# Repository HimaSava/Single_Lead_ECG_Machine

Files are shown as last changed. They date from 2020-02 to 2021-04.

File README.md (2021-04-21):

# Single_Lead_ECG_Machine

This project started as the project component for my subject analog electronic communcation that I took in my Winter Sem 2019.

The project uses 3 wires to be connected to the paitent as to aquire the ECG waveform from 2 of them and the third used as ground. The Circuit uses basic filteration techniques to get rid of the surrounding noise and amplify the signal to be effectively seen on a osciloscope.

## Components of the Circuit and thier purpose:
#### 1. Instrumentational Amplifier:
The ECG signal received from the body is in milivolts and thus needs to be amplified in order to be captured by any instrument. An instrumentational amplifier is used rather than an normal amplifier as it helps limit the noise entering the system due to its differential amplification functionality.

#### 2. High Pass Filter:
A high pass filter is used to get rid of the lower frequencies caught up in the system. This filter also takes care of the dc voltage in the system, avoiding saturation of the furthur amplification stages. An second order filter is used for better results.

#### 3. Low Pass Filter:
A low pass filter as expected is again used to remove the unnecessary frequencies. A second order filter is used for optimised results.

#### 4. Notch Filter:
A notch filter is a filter that helps remove a very narrow band of frequencies. In our case it is tuned for 50Hz. This is the standard AC freq. in the Indian power supply and thus is present in the surrounding in great quantities. This is caught in the system and can lead to distorting the final waveform significantly.

## Components used:
#### 1. OpAmps TL074CN (Highly advised for this experiment)
#### 2. Registers 
#### 3. Bi-Directional Capacitors(Ensure the cap are not uni-directional as the ECG signal is bi-directional)

## Tools used:
1. Multisim - To design and test the basic circuit.
2. Eagle AutoCAD - To design the custom PCB and help design the soldering breadboard circuit layout.

## Scope for improvement:
#### Currently the waveform is only viewed using an osciloscope, but in future I want to connect the system to my laptop and record data using it. For this a few more components need to be added to the ciruit as listed below:

1. Level Shifter:
An Analog to digital converter can only deal with positive voltages thus the waveform needs to be shifted upwards to convert the negative part of the ECG signal to positive.

2. A2D converter:
An analog to digital converter is needed as our output is analog but the inut by the microcontroller can only be digital.

3. Microcontroller:
An microcontroller will be able to accept the input from the A2D converter and using Communcation protocols as Serial(RS232), ICP, etc transfer the data to the PC.

4. PC end program:
Once we start recieving the data from the circuit it is important to store the same and show the output in the most familier fashion of an graph. This will be handled by an PC end program.

#### A custom designed PCB will also help in reducing the noise in the system.

### Pls find the attached in the folders above:
1. Individual Circuits of the filters
2. The complete Circuit for the ECG.
3. Eagle files for the PCB (Gerber files will be added shortly)
4. Output waveforms captured by the circuit and the final pictures of the circuit.

Manufactured Layout V1.0

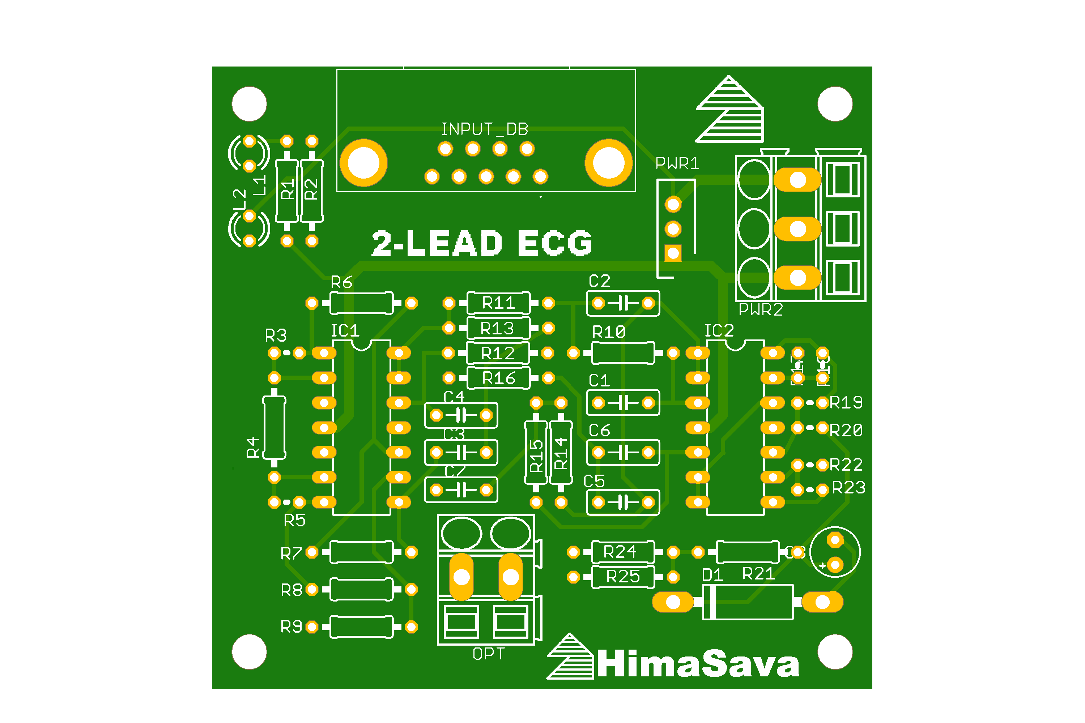
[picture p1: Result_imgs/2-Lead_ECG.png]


Output!!

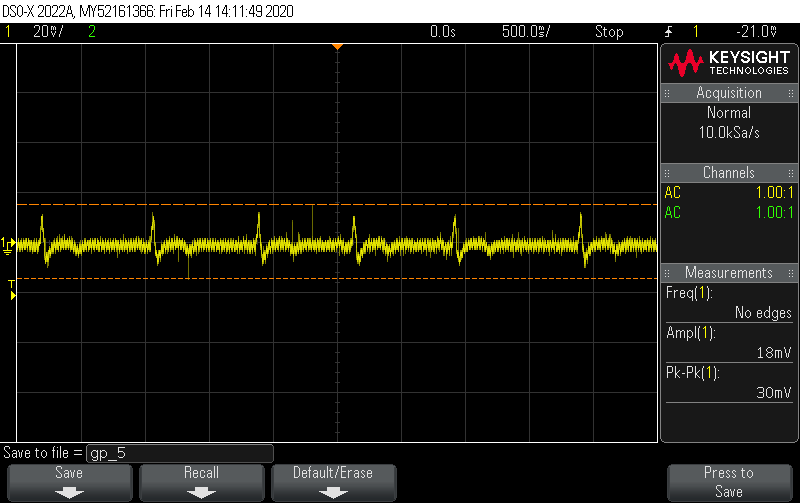
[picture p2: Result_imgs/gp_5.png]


#### -Himanshu Savargaonkar
##### P.S. Shoutout to Praneeth G (gp201) for being the test subject for all the live tests conducted in the debugging phase :)

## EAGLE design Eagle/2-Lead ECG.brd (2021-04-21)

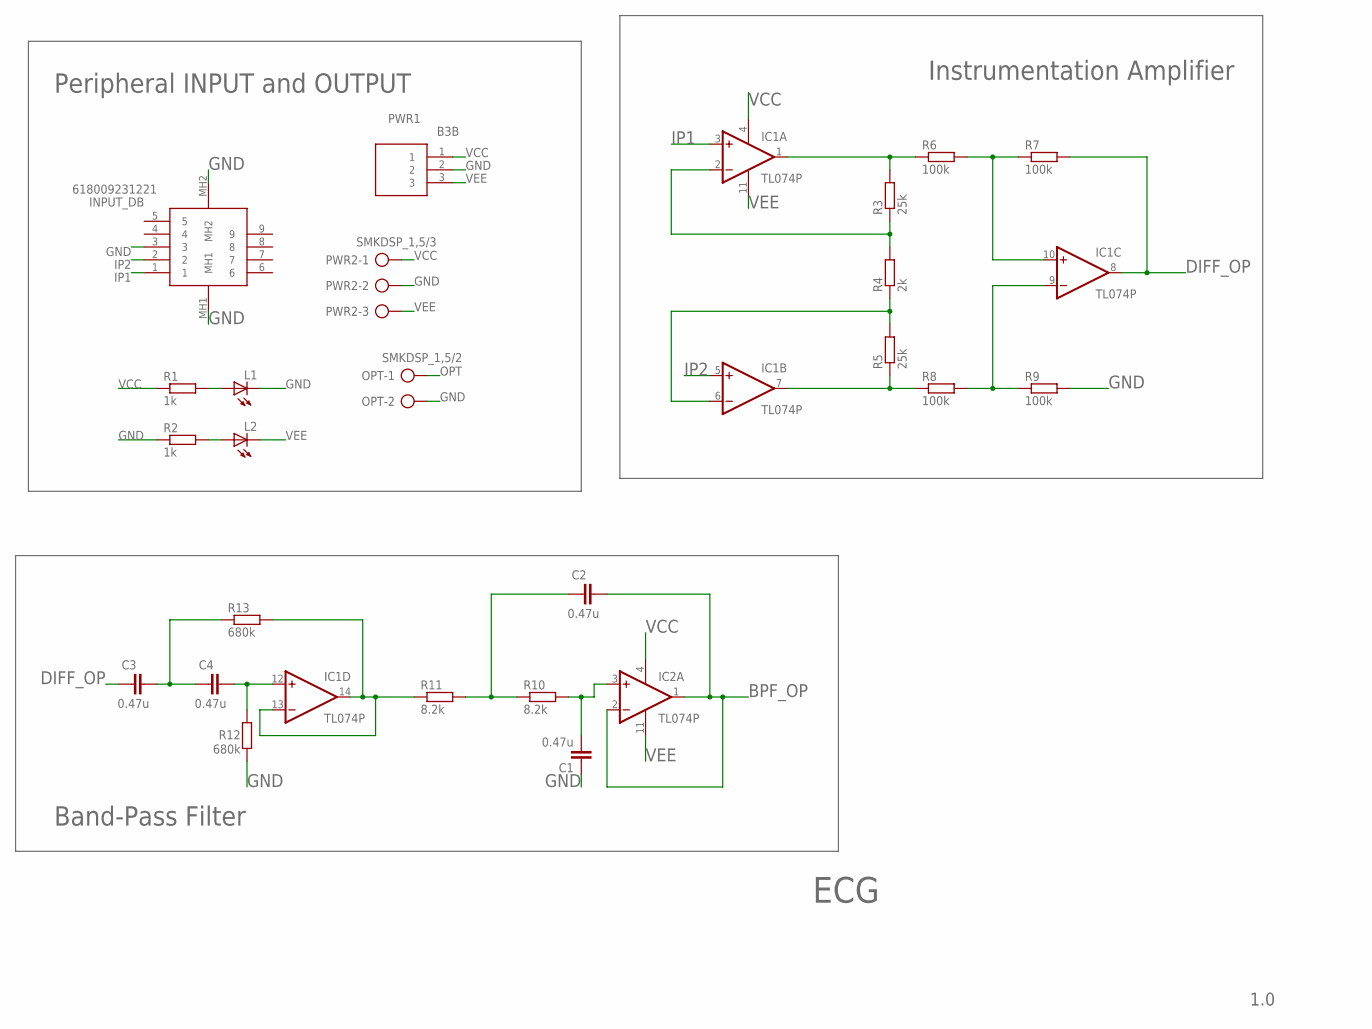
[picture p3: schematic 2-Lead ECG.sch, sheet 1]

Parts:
C1, C2, C3, C4: 0.47u; C050-025X075
IC1, IC2: TL074P; DIL14
INPUT_DB: 618009231221
L1, L2: LED3MM
OPT: SMKDSP_1,5/2
PWR1: B3B; SHDR3W64P0X250_1X3_1000X380X60
PWR2: SMKDSP_1,5/3
R1, R2: 1k; 0207/10
R3, R5: 25k; 0204V
R4: 2k; 0207/10
R6, R7, R8, R9: 100k; 0207/10
R10, R11: 8.2k; 0207/10
R12, R13: 680k; 0207/10

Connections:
BPF_OP: C2.2, IC2.1 (OUT), IC2.2 (-IN); also elsewhere on the board
DIFF_OP: C3.1, IC1.8 (OUT), R7.2
GND: C1.1, INPUT_DB.3, INPUT_DB.MH1, INPUT_DB.MH2, L1.K (C), OPT.2, PWR1.2, PWR2.2, R2.1, R9.2, R12.1; also elsewhere on the board
IP1: IC1.3 (+IN), INPUT_DB.1
IP2: IC1.5 (+IN), INPUT_DB.2
unnamed: L1.A, R1.2
unnamed: L2.A, R2.2
unnamed: IC1.1 (OUT), R3.2, R6.1
unnamed: IC1.2 (-IN), R3.1, R4.2
unnamed: IC1.6 (-IN), R4.1, R5.2
unnamed: IC1.7 (OUT), R5.1, R8.1
unnamed: IC1.10 (+IN), R6.2, R7.1
unnamed: IC1.9 (-IN), R8.2, R9.1
unnamed: C3.2, C4.1, R13.1
unnamed: IC1.13 (-IN), IC1.14 (OUT), R11.1, R13.2
unnamed: C4.2, IC1.12 (+IN), R12.2
unnamed: C2.1, R10.1, R11.2
unnamed: C1.2, IC2.3 (+IN), R10.2
OPT: OPT.1; also elsewhere on the board
VCC: IC1.4 (V+), IC2.4 (V+), PWR1.1, PWR2.1, R1.1; also elsewhere on the board
VEE: IC1.11 (V-), IC2.11 (V-), L2.K (C), PWR1.3, PWR2.3

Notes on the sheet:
Peripheral INPUT and OUTPUT
Instrumentation Amplifier
Band-Pass Filter
1.0
ECG

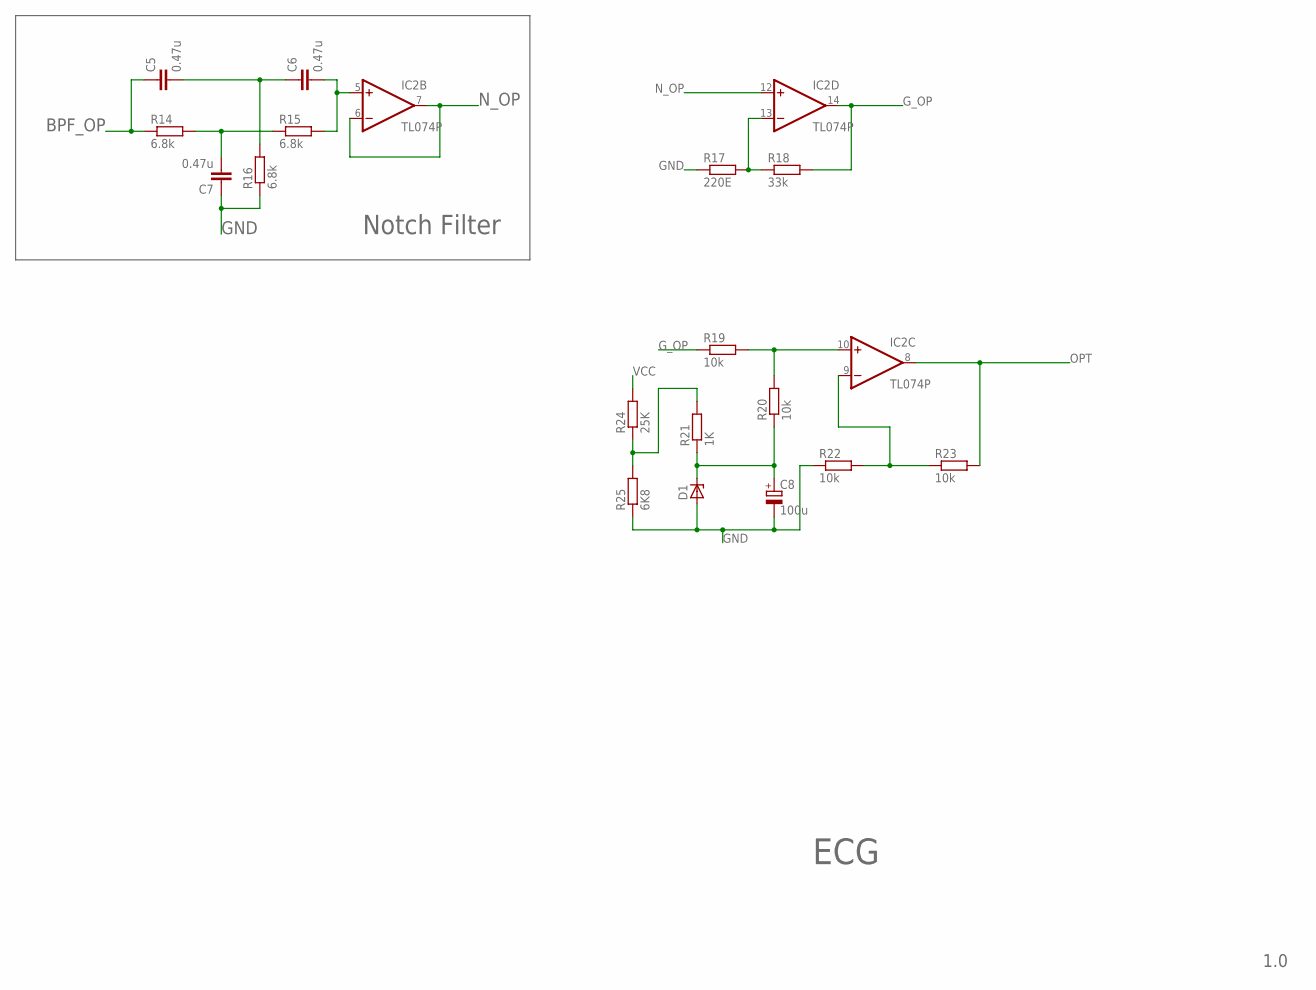
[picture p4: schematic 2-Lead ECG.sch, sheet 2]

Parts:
C5, C6, C7: 0.47u; C050-025X075
C8: 100u; E2,5-5
D1: ZENER-DIODEC1702-15; C1702-15
IC2: TL074P; DIL14
R14, R15, R16: 6.8k; 0207/10
R17: 220E; 0204V
R18: 33k; 0204V
R19, R20, R22, R23: 10k; 0204V
R21: 1K; 0207/10
R24: 25K; 0207/10
R25: 6K8; 0207/10

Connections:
BPF_OP: C5.1, R14.1; also elsewhere on the board
GND: C7.1, C8.-, D1.A, R16.1, R17.1, R22.1, R25.1; also elsewhere on the board
G_OP: IC2.14 (OUT), R18.2, R19.1
unnamed: IC2.13 (-IN), R17.2, R18.1
unnamed: C5.2, C6.1, R16.2
unnamed: C6.2, IC2.5 (+IN), R15.2
unnamed: C7.2, R14.2, R15.1
unnamed: IC2.10 (+IN), R19.2, R20.2
unnamed: IC2.9 (-IN), R22.2, R23.1
unnamed: R21.2, R24.1, R25.2
unnamed: C8.+, D1.C, R20.1, R21.1
N_OP: IC2.6 (-IN), IC2.7 (OUT), IC2.12 (+IN)
OPT: IC2.8 (OUT), R23.2; also elsewhere on the board
VCC: R24.2; also elsewhere on the board

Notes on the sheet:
Notch Filter
ECG
1.0

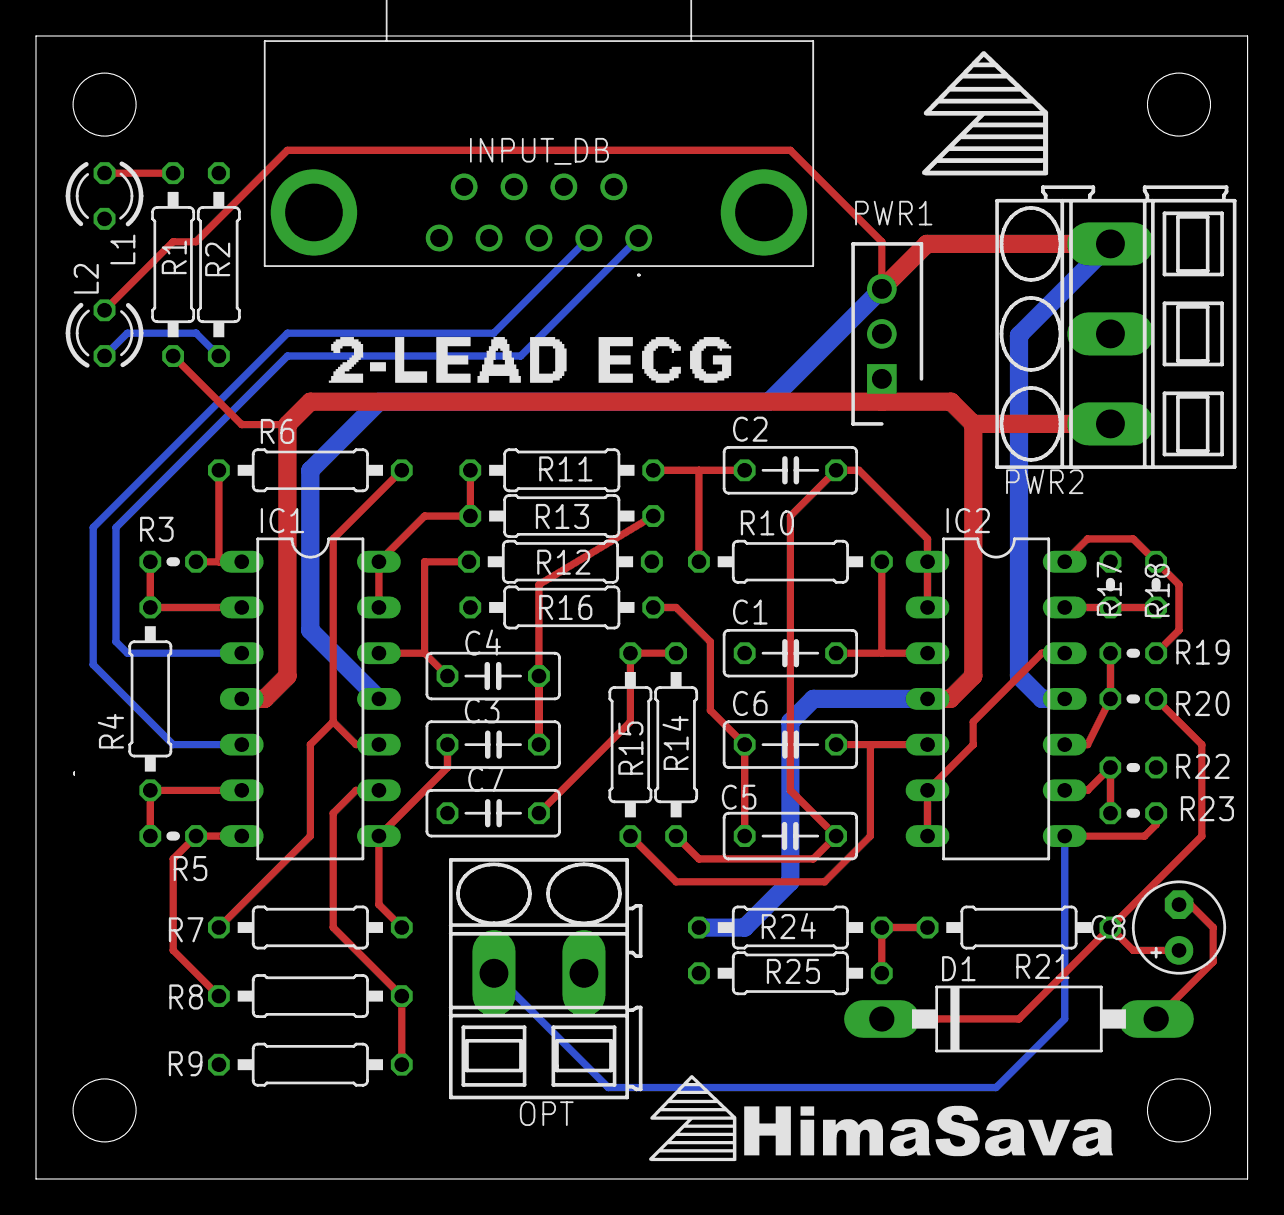
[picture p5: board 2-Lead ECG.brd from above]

Board: 2 copper layers, 67.3 x 63.5 mm, 42 parts (0 on the bottom side), 31 nets.

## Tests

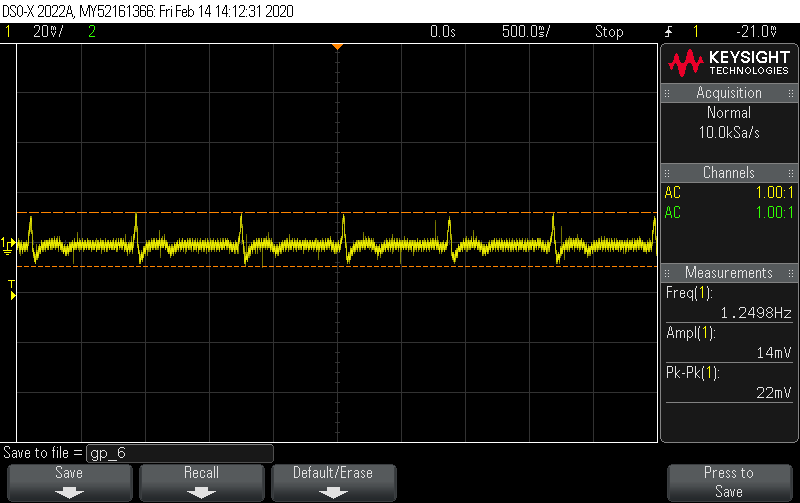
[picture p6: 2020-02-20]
Result_imgs/gp_6.png

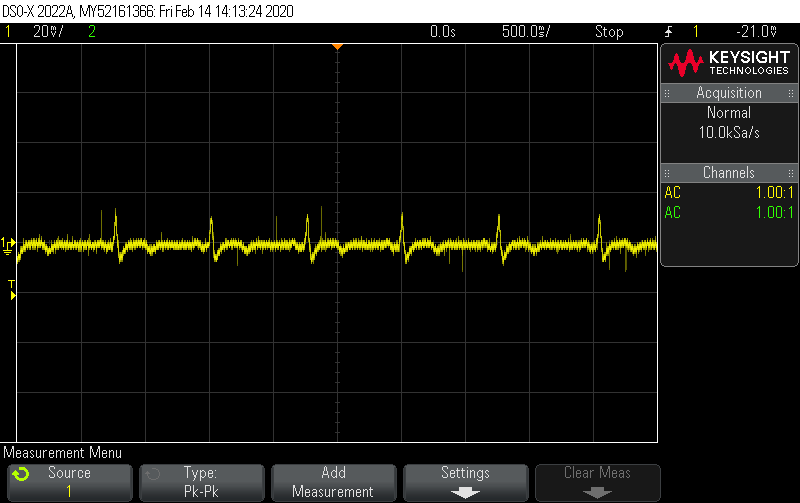
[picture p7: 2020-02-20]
Result_imgs/gp_7.png

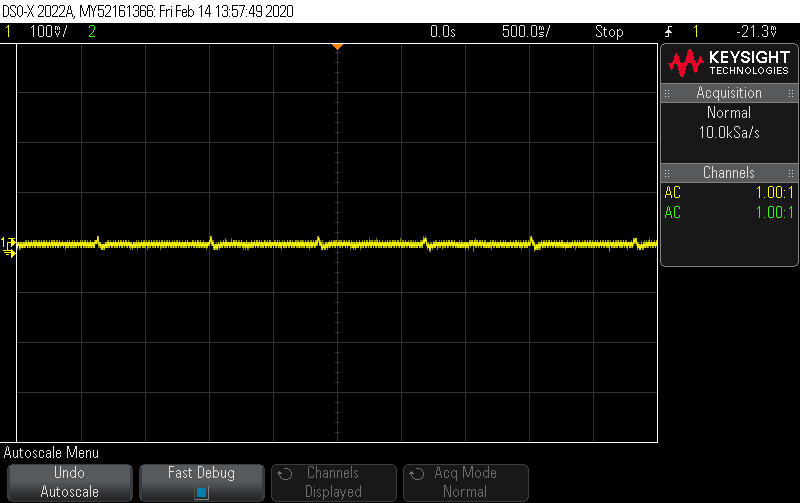
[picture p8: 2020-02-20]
Result_imgs/gp_0.png

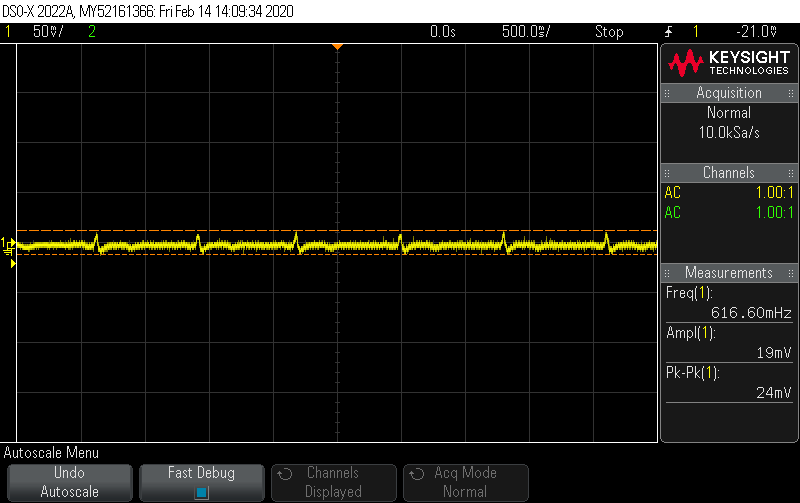
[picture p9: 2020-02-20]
Result_imgs/gp_4.png

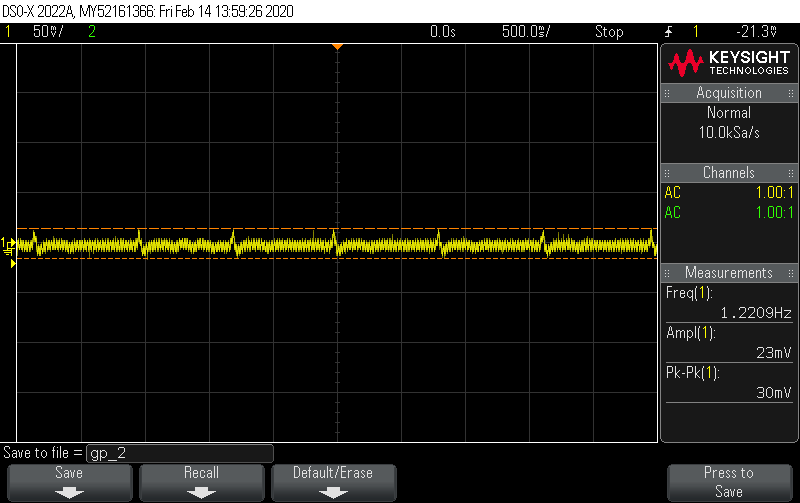
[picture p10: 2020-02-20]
Result_imgs/gp_2.png

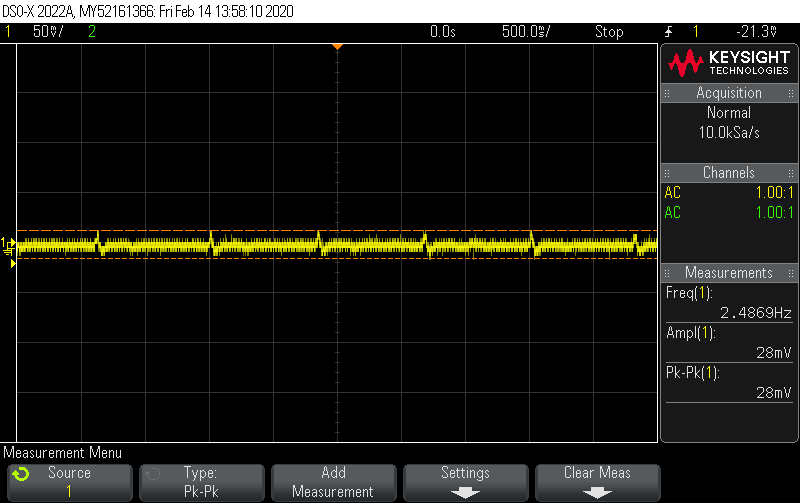
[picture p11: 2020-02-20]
Result_imgs/gp_1.png
